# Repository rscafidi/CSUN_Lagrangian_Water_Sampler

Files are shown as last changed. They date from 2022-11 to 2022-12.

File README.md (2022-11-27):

# CSUN Lagrangian Water Sampler
Microcontroller code for the CSUN Lagrangian Water Sampler Project

This project was to fix a maker device created for California State University, Northridge.  The device runs using a Arduino compatible Mini Ultra 8Mhz microcontroller with ATmega328P processor.  The device controlls two peristaltic water pumps for two periods of time during each day.  Based on comments in the original code, it was originally created by Vincent Moriarty on June 29, 2016.  Since that time, the real time clock (DS3231) used to keep time in-between board power failures had run out of power causing the clock to reset.  As such, the pumps stopped working on their intended schedule.  During troubleshooting, the device was rendered inoperable and users were unable to reset the time.

The device was also created without any technical documentation.  This project scope was to understand the original circuit, troubleshoot the software and hardware, and restore it to original functionality.  Additional tasks are to document the circuit, components, and code and create a manual for how to reflash the code and restore it to operating state.

The code was completely rewritten but the original functionality was mostly retained.  The major change is that the new code will check for the Oscillator Stop Flag bit every time the controller boots.  This bit keeps track of when the real time clock oscillator stops, meaning the time is most likely not accurate.  If the OSF bit is detected as logical 1, the board goes into a LED flash loop to alert the user there is a problem.

Several other changes have been made to make the code easier to understand and modify.  The original code is retained in this repository for historical records.

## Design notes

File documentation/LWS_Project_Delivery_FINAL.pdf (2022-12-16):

1 | P a g e

# LAGRANGIAN WATER SAMPLER

PROJECT DELIVERY – FINAL DELIVERY

PREPARED FOR:

## CALIFORNIA STATE UNIVERSITY, NORTHRIDGE

Prepared by:

Richard E Scafidi – Software Engineer

richard@scafidi.dev

2 | P a g e

TABLE OF CONTENTS

3 | P a g e

ORIGINAL PROPOSAL

EXECUTIVE SUMMARY

The Lagrangian Water Sampler (LWS) is a custom-made device, created under the direction of California State University, Northridge (CSUN), who is hereon known as the Customer in this proposal. The LWS is used for automated collection of water samples at specific time intervals throughout each day, indefinitely while the onboard battery is still powering the device. The device was designed to be fully submerged under water at depths of approximately two to three meters. The device uses an Arduino based microcontroller and electronic components to control two water pumps on specifically programmed intervals. The device is powered by several large removable batteries. Recently, the device has become inoperable and troubleshooting attempts that were made to restore the device were not successful. CSUN is requesting to have the device restored to original functionality, and to provide technical documentation for the electronic circuitry, component design, and microcontroller code maintenance procedures to facilitate future maintenance efforts.

PROJECT SCOPE

The scope of this project is as follows:

- Examine, troubleshoot, and understand the original electronic circuitry.
- Design, assemble and test fixes to restore the system to functionality described in the Functional Requirements section.
- Document electronic circuit design and functionality.
- Document microcontroller source code and code flashing/building procedures.
- Document all electronic components within the system including part type, number and function/use case where possible.
- Testing is limited to electronic components and microcontroller programming only. The original waterproof housing will not be provided for testing and as such will not be a part of the test cases.
- There will be no continued support for the device after delivery of the functional device and documentation under this proposal.

4 | P a g e

PROJECT DELIVERABLES TIMELINE
The estimated timeline for deliverables is as follows:
Deliverable Name | Description | No Later Than Date
Feasibility Report | This is a single document that outlines the technical work that will need to be done after examining the device, and will deliver a statement on whether or not the planned project objectives can be delivered by the desired final deliverable date. | 31 August 2022
Project Update Briefs | If the project continues beyond the Feasibility date, project update briefs will be held on a recurring basis. These will be written reports that outline the current state of the project including progress, delays, and any other information. It will also include demonstrations of any functionality in order to ensure the device is being designed to meet the customer’s expectations. | Bi-weekly for the duration of the project
Post-testing Report and Demonstration | When the engineering team determines the project has met all documented requirements, a final testing report will be delivered. This report will be accompanied by a product demonstration to validate customer requirements have been met. | 15 November 2022
Documentation Validation | If the device is validated by the customer, the next deliverable will be product documentation to include parts lists, electronic diagram documentation, troubleshooting documentation, and code documentation. | 1 December 2022
Delivery of hardware and documentation artifacts | After the documentation is validated, the device will be returned to the customer along with all documentation artifacts. At this time the project will be considered closed. | 15 December 2022

Changes to the project may affect the above timeline. Adding new requirements may push the project beyond the desired completion timeline of December 2022. A best effort will be made to inform the customer of any such potential impacts.

5 | P a g e

BUDGET
This project is estimated to require between thirty (30) to forty (40) hours of engineering time for troubleshooting, repair, documentation and testing of the product. It will also potentially require acquisition of new electronic components. The budget estimates are outlined below. For all material costs, an estimate is given now. At the time of delivery and payment, actual receipts for any material item will be provided and the cost will be adjusted to match. The material estimates below are conservative estimates.
Item | Cost per Unit | Quantity / Type | Total
Engineering Time | $45 | 35 Hours | $1575
Electronic components | $150 | - | $150
Grant Total Estimated | | | $1725

If, after the project feasibility report, it is determined that the time estimated will vary plus or minus 10%, the Customer will be notified for approval to continue.

6 | P a g e

FUNCTIONAL REQUIREMENTS
Functional requirements are specific requirements that the system must meet to be considered complete. Below is a list of functional requirements.
- The system must be functional in an underwater environment at depths of two to three meters. This requirement will not be tested due to original housing unavailable for testing. No modifications are planned that would interfere with the original housing waterproofing capabilities.
- The system must run on the provided battery supply which outputs 12.5 volts.
- The system must use local time to operate on the following schedule:
o Activation of Pump 1 from local time 10:00 AM until 4:00 PM
o Activation of Pump 2 from local time 10:00 PM until 4:00 AM

NON-FUNCTIONAL REQUIREMENTS
Non-functional requirements are requirements not specifically related to a function of the device itself. Below is a list of non-functional requirements.
- The documentation provided will be in English.
- The documentation provided will include technical and non-technical aspects of the system, including each component, the function and use case within the system, and technical documentation for any source code provided.

7 | P a g e

DELIVERY REVIEW

DELIVERABLE SCHEDULE RESULTS

Deliverable Name | No Later Than Date | Outcome
Feasibility Report | 31 August 2022 | No report was generated. Verbal discussion with the customer resulted in simply fixing the functionality rather than redesigning the entire product. Due to the dramatic reduction in scope, a full report on how feasible a new product would be and what it would look like was not necessary.
Project Update Briefs | Bi-weekly for the duration of the project | We did not adhere to the bi-weekly updates on a regular basis, but we did provide casual updates on progress.
Post-testing Report and Demonstration | 15 November 2022 | This timeline was not achieved with the Customer, but extensive testing was done in-house by this date.
Documentation Validation | 1 December 2022 | All documentation was submitted to Customer on 28 November for validation.
Delivery of hardware and documentation artifacts | 15 December 2022 | One control unit will be delivered by 1 December and the second unit will be delivered by 20 December, pending any feedback from the Customer. Customer notified of final delivery and the new date is acceptable.

TOTAL COST TO DATE

Item | Actual Cost | Actual Quantity | Actual Total
Engineering Time | $45 | 32 | $1,440
Electronic components | $190.37 | - | $190.37
Shipping | $24.27 | - | $24.27
Grand Total | | | $1,654.64

*Note that extra materials were ordered and will be delivered to Customer for future repairs if necessary. Some components ordered will be retained for testing.

8 | P a g e

USER ACCEPTANCE TESTING

One Lagrangian Water Sampler unit was returned to the Customer by 1 December to validate project deliverables. The project deliverables consist of all documentation, along with one unit to test in the field.

Field testing was conducted, and no issues were reported. User acceptance testing considered to be completed. Second unit shipped on 16 December and will arrive no later than 20 December.

9 | P a g e

PRODUCT DOCUMENTATION

Below is a summary of the documentation provided as part of this project.

Appendix A – Circuit Diagram

Appendix B – Testing Report

Appendix C – Troubleshooting Manual

Appendix G – Bill of Materials

Appendix H – Material Cost Receipts

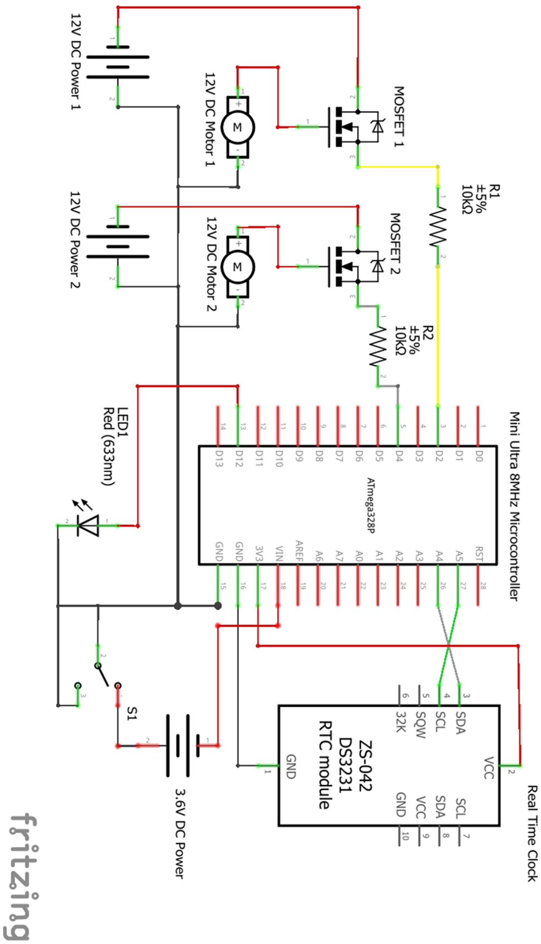
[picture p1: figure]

10 | P a g e

APPENDIX A – CIRCUIT DIAGRAM

11 | P a g e

APPENDIX B – TESTING REPORT

CONTROL UNIT 1 TEST RESULTS
Component | Results
LED | Pass
MOSFET Transistor 1 | Pass
MOSFET Transistor 2 | Pass
DS3231 Real Time clock | Pass
3v Clock battery | Fail
Microcontroller pin 3 | Fail
Microcontroller pin 5 | Pass
Microcontroller VIN | Pass
Microcontroller FTDI Header | Pass
Microcontroller Ground | Pass
Microcontroller pin A4 | Pass
Microcontroller pin A5 | Pass
Microcontroller 3.3v Power Supply | Pass

CONTROL UNIT 2 TEST RESULTS
Component | Results
LED | Pass
MOSFET Transistor 1 | Pass
MOSFET Transistor 2 | Pass
DS3231 Real Time clock | Pass
3v Clock battery | Fail
Microcontroller pin 3 | Pass
Microcontroller pin 5 | Pass
Microcontroller VIN | Pass
Microcontroller FTDI Header | Pass
Microcontroller Ground | Pass
Microcontroller pin A4 | Pass
Microcontroller pin A5 | Pass
Microcontroller 3.3v Power Supply | Pass

The components were tested on both pump control devices provided. For one control device, the only defective part was the 2032 3v watch battery powering the DS3231 real time clock. For the other, there is a voltage leak within the A328P processor causing pin 3 to be in HIGH state while the board is powered. This in turn keeps the MOSFET open, which will keep pump 1 on. A replacement microcontroller was ordered and soldered in place to restore functionality to the second controller. The 2032 3v watch battery was also bad on the second controller. Both watch batteries were replaced.

12 | P a g e

The code was completely rewritten for several reasons. First, the real time clock can track when a power failure has occurred, a feature which was previously not utilized. This feature was incorporated into the refactoring of the code to put the controller into a state such that normal operation will not proceed until the problem is addressed. The LED on pin 12 will flash continuously, which should alert the user that something is wrong with the controller. The maintenance manual walks through how to troubleshoot and restore the device to working order.

The second reason for refactoring is to make the code more readable. Detailed comments have been provided within the code to explain key portions of functionality. Additionally, the time control structure was rewritten to make it simpler to understand and modify. Outside of the comments, the code itself has been written in a manner to increase self-documentation, which will make it easier for users to read and change if necessary.

The final change relates to the inclusion of preprocessor directives to change the program execution behavior by simply commenting or uncommenting single variables. This again makes it easier to put the microcontroller into various testing states as well as enhancing the method of syncing the clock. The following page contains steps used to test each component with the new code.

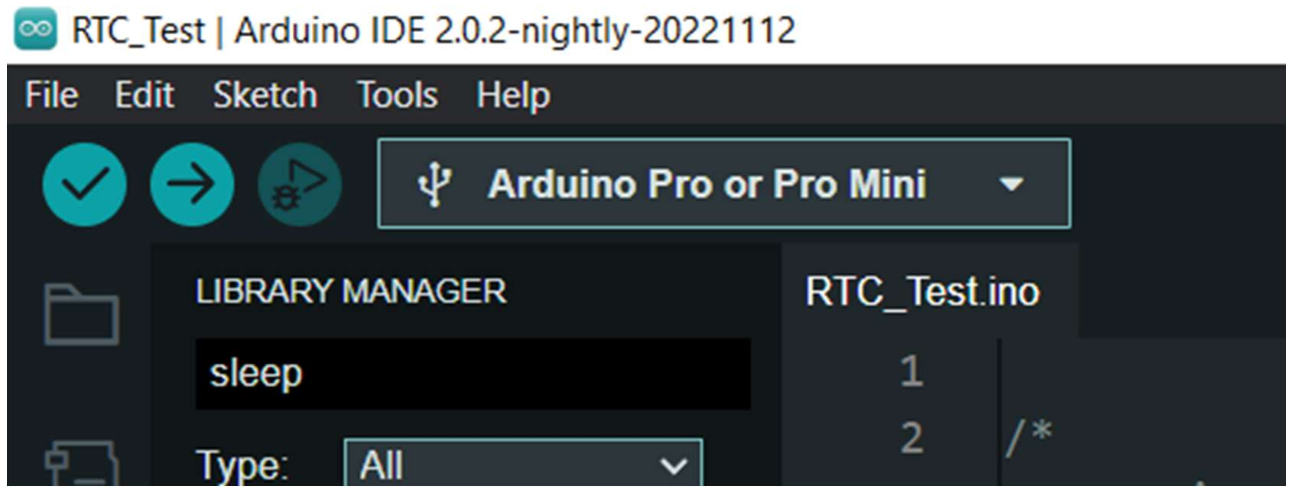
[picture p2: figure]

13 | P a g e

APPENDIX C – TROUBLESHOOTING MANUAL

TESTING DEPENDENCIES
Dependencies used in testing:
Adafruit RTClib library v2.1.1
Adafruit SleepyDog library v1.6.3
Standard Wire library

FLASHING CODE TO THE MICROCONTROLLER
The code is available on github at the following repository: https://github.com/rscafidi/CSUN_Lagrangian_Water_Sampler
Setting up Arduino IDE and loading the Pump Timer sketch
1. Open the Pump_Timer_MOSFET_Sleeper.ino sketch within the Arduino IDE.
a. Launch Arduino IDE, then go to File > Open > navigate to the .ino file
2. Set the IDE to the controller model and processor.
a. Connect the microcontroller to your PC with the USB header pin connector.
b. Click the COM port selector dropdown

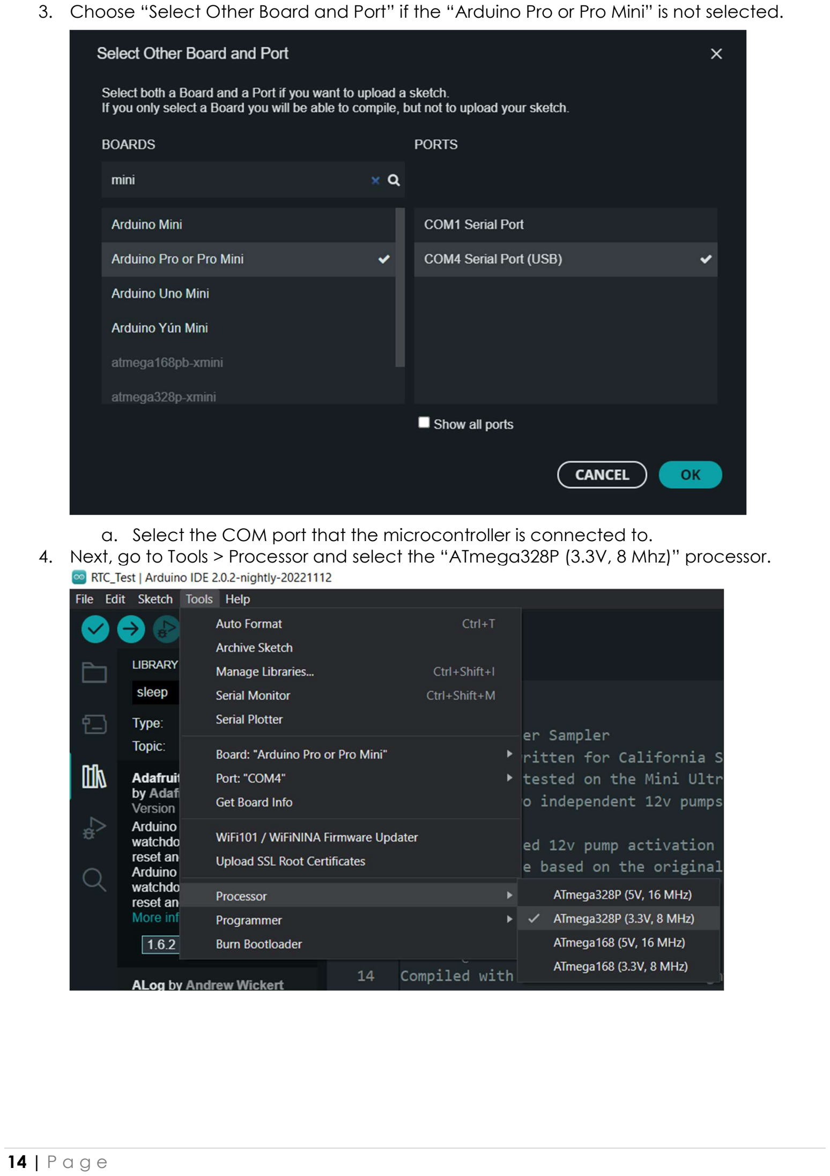
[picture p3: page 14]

14 | P a g e
3. Choose “Select Other Board and Port” if the “Arduino Pro or Pro Mini” is not selected.
a. Select the COM port that the microcontroller is connected to.
4. Next, go to Tools > Processor and select the “ATmega328P (3.3V, 8 Mhz)” processor.

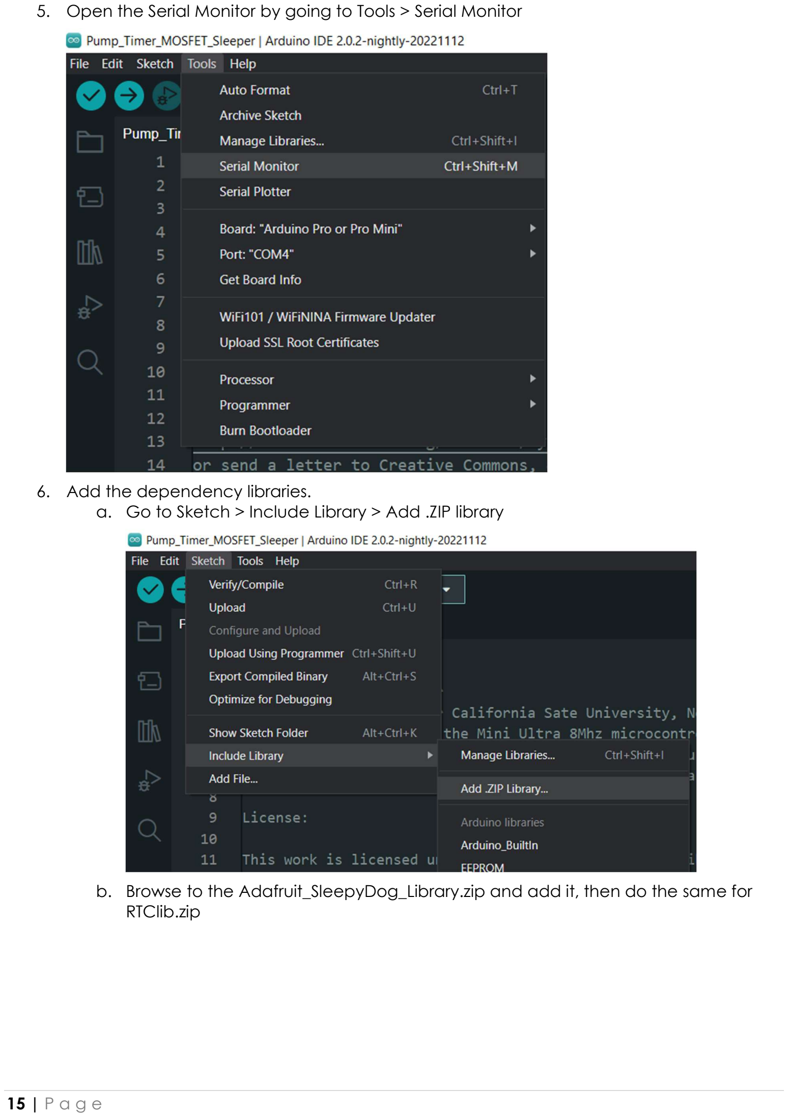
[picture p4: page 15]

15 | P a g e

### 5. Open the Serial Monitor by going to Tools > Serial Monitor

6. Add the dependency libraries.
a. Go to Sketch > Include Library > Add .ZIP library
b. Browse to the Adafruit_SleepyDog_Library.zip and add it, then do the same for RTClib.zip

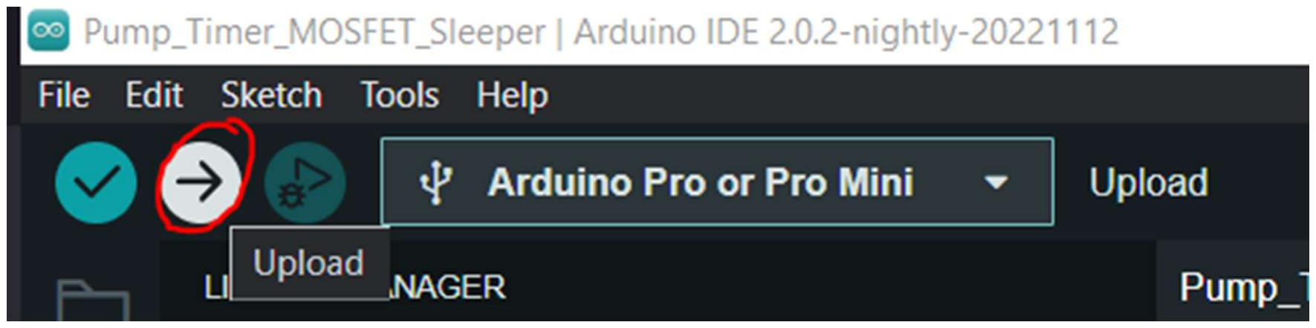
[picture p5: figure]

16 | P a g e
c. Note you can also install libraries via the library manager within the Arduino IDE but they were included in case dependencies change in the future.

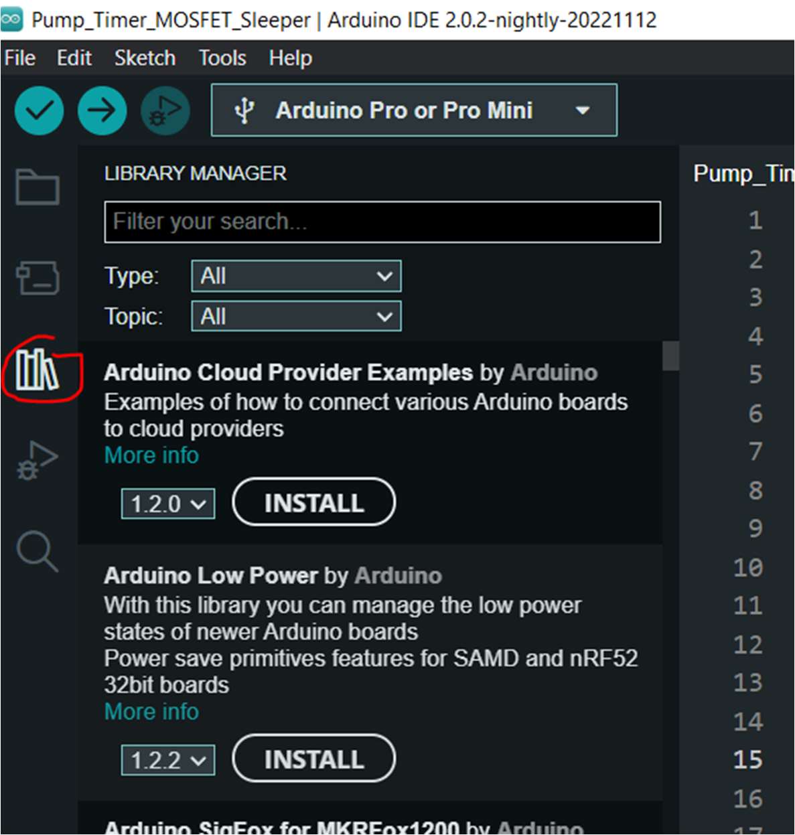
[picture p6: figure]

7. Put the controller into CODE_DEBUG_MODE by uncommenting line 36.
8. Click the Upload button to compile and load the program onto the microcontroller.
9. The Output tab will give you status on the compilation and upload. Note that if you see “Access is denied” on your COM port, try uploading again. Sometimes the COM port is busy and won’t let the PC talk over it temporarily. It could also be giving you that error if you have the wrong COM port selected.

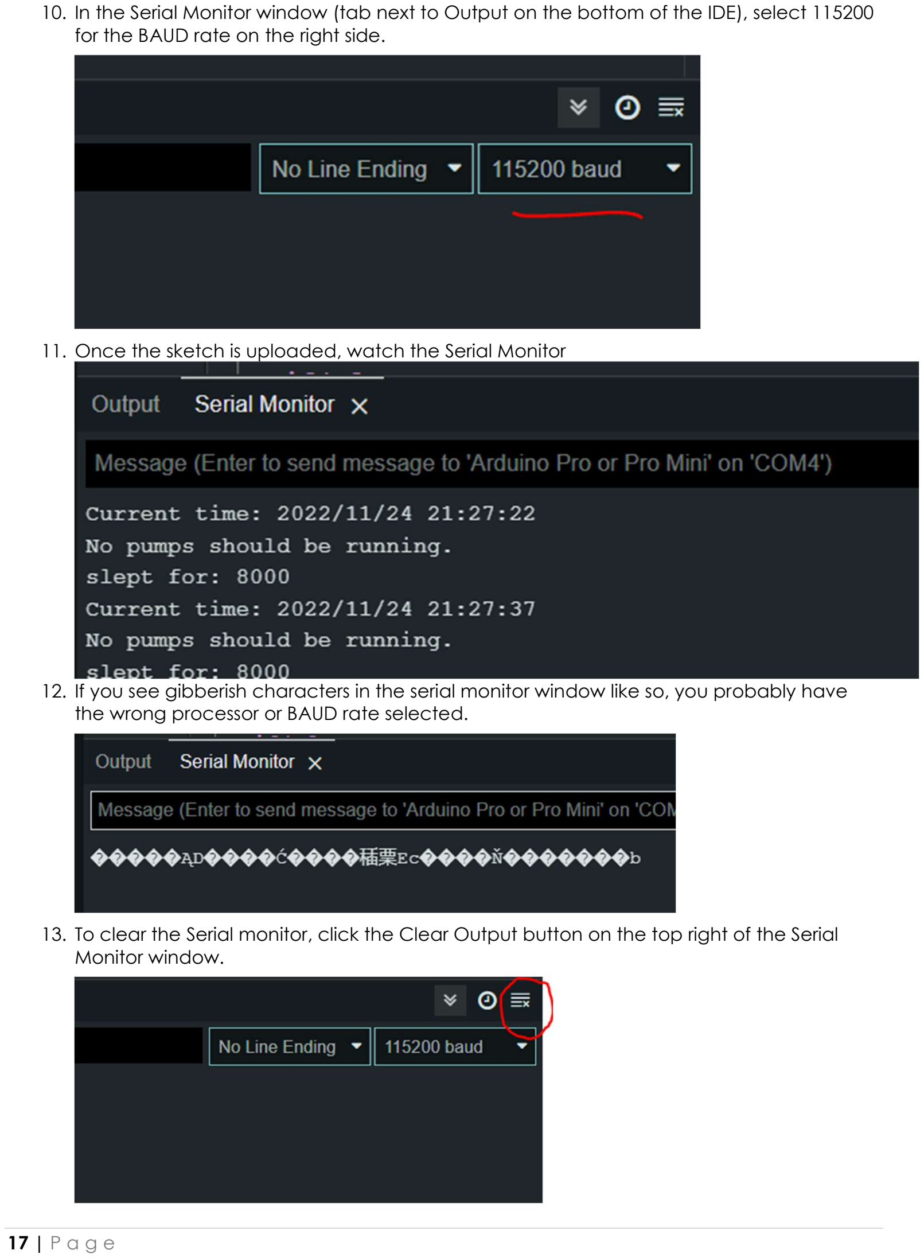
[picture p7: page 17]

17 | P a g e
10. In the Serial Monitor window (tab next to Output on the bottom of the IDE), select 115200 for the BAUD rate on the right side.

### 11. Once the sketch is uploaded, watch the Serial Monitor

12. If you see gibberish characters in the serial monitor window like so, you probably have the wrong processor or BAUD rate selected.
13. To clear the Serial monitor, click the Clear Output button on the top right of the Serial Monitor window.

18 | P a g e

LED LIGHT STATUS CODES

The LED light connected to pin 12 will flash in different patterns indicating various conditions of the controller.

LED Pattern | Meaning
Rapid blinking, not stopping | The microcontroller has encountered an error state, or the clock oscillator has been interrupted.
5 sets of 3 bursts | The microcontroller is in circuit debugging mode or clock sync mode. Program execution will not continue in these modes. Code must be recompiled and flashed with the control variables commented out.
20 bursts | The pumps are reporting as on during the scheduled hours they should be inactive. Troubleshooting required.
Single blink every ~10 minutes (seemingly no blink) | The microcontroller is operating normally and the pumps are both off.
Single blink every ~5 seconds | The microcontroller is operating normally and one of the pumps is active.

SWITCHING CONTROLLER MODES

The controller has three non-standard modes programmed that are controlled by commenting and uncommenting the associated control variables, starting on line 30. The first mode (CODE_DEBUG_MODE) will compile the code to produce Serial output strings that can be helpful for debugging so you can view the Serial Monitor for information. The second mode (CIRCUIT_DEBUG_MODE) will compile the code such that pump 1 and 2 will alternate being on for 5 seconds each. This can be useful for troubleshooting during times that the pumps won’t normally run. The third mode (CLOCK_SYNC_MODE) is used when the DS3231 real time clock has encountered a power interruption and needs to be resynced. This mode will reset the flags indicating power interruption occurred and will sync the time with the date and time that the application was last programmed. Note that for CIRCUIT_DEBUG and CLOCK_SYNC modes, it is critical to recompile the code with these modes commented out or the normal state will never resume. CODE_DEBUG_MODE can be used during normal operation, but it should be commented out as well when you are not actively debugging things.

19 | P a g e

CHANGING THE SCHEDULE BEHAVIOR

The original requirements specified that pump 1 should run from 10AM until 4PM, and pump 2 should run from 10PM until 4AM. The current program will accomplish this schedule. It is possible to change the schedule, but it may require some slight re-programming of the time control logic.

Constants used for the start and stop times for each pump are defined on lines 74 to 78. Shifting the hours is relatively easy. However, if you must add minutes to the schedule, you will have to evaluate the pump control logic and add in the checks for minutes. The current minute is accessible using now.minute() similar to how the hour was retrieved. The control logic is defined on lines 455 to 480.

With the current control logic, the pumps will activate within 10 minutes of the appropriate hour changing. It is possible to reach a higher degree of accuracy if required but it will take more power.

CHANGING BOARD SLEEP TIME
The pump activation will be plus or minus the setting for sleep minutes (constant variable SLEEP_SECONDS defined on line 79). This equates to 10 minutes, which appears to be the previous behavior based on previous code. This means that, in the worst case, the pump could activate up to 10 minutes past the start time. If higher accuracy is desired, simply reduce the SLEEP_SECONDS variable and recompile the code. Note that lower sleep time will increase power consumption.

TROUBLESHOOTING
1. Edit code to uncomment line 45, to enable CIRCUIT_DEBUG_MODE.
2. Compile and upload the code to the microcontroller.
3. Ensure a 12v power source is connected to the MOSFET transistors.
4. Verify the 5 bursts of 3 flashes on the LED, indicating the controller is in a special control mode.
a. Each pump will cycle ON for 5 seconds before repeating the flash cycle. Check that each pump operates.
b. If the LED never illuminates, check the board power on the VIN pin, a minimum of 3.3v is required.
c. If the board is powered and the code successfully uploaded but there are no LED flashes, check the signal on pin 12. If pin 12 never goes HIGH, there may be a problem with the microcontroller.

### 5. If the pumps are not connected, use a multi-meter to check the voltage on the output

side of the MOSFET transistor. Place one lead on GROUND and place the other on the positive side of the MOSFET transistor output. Wait for the controller to cycle, a minimum of 7 seconds if it is not active when you first check.

20 | P a g e
a. If the output never reads 12v, trace the signal from pin 3 (or 5). If the voltage is cycling on the pin wire but the output never cycles to 12v, there is a problem with the MOSFET transistor, and it should be replaced.
6. Repeat for the second MOSFET transistor.
7. Check the DS3231 onboard LED. It should be illuminated when the board is powered.
a. If desired, put the board into CODE_DEBUG_MODE, compile and upload, and watch the serial output to ensure the time is correct.
b. If time needs to be corrected, uncomment the CLOCK_SYNC_MODE control variable, and flash the code again.
i. IMPORTANT: You must comment out the CLOCK_SYNC_MODE control variable and flash the code again before the microcontroller boots again. When CLOCK_SYNC_MODE is active, it will always use the last compiled time to set the real time clock. If you wait an hour and the board reboots, the clock will now be off by one hour.
8. Assuming you have been testing while the microcontroller is connected to the PC, restore the normal operational mode by commenting out all control variables and flashing the code again. Remove the controller from the USB/FTDI header and connect to 3.6v battery supply.
a. Verify the LED is flashing once every 15 seconds if the time is outside of pump operational hours, or once per 5 seconds if the time is within pump operational hours.
9. Ensure the switch works to turn the main board off.
10. Turn the main board back on. Ensure the LED pattern continues to read a normal state.

### 11. If the LED ever enters a quick pulse that does not stop, an error state has been

encountered.
a. Most likely, the real time clock has lost power.
b. Check the 3v battery supply, replace if necessary.
c. Flash code again with CLOCK_SYNC_MODE and CODE_DEBUG_MODE uncommented.
d. Watch the serial output and make sure it goes back to a normal state.
e. Comment the special control variables and flash code, check LED again and power cycle the board.
12. If the board is properly resetting the clock registers (success messages when board is in CLOCK_SYNC_MODE) but the real time clock is losing power in between board cycles with a known good 3v battery, this could indicate a problem with the real time clock. Recommend replacing the module.

21 | P a g e

APPENDIX D – BILL OF MATERIALS

Below are the items that comprise the Lagrangian Water Sampler. These parts were provided by CSUN and in some cases, replacements were ordered. This list includes each component with applicable part numbers where possible.

Item Friendly Name | Part Number or ID | Functional Description
Mini Ultra 8Mhz Microcontroller | ATMega328P 8Mhz 3.3v | Microcontroller for executing code to control LED and pumps
MOSFET Transistor x2 | FQP30N06L | Transistor to open circuit to 12V power in order to power the pumps
Real Time Clock module | DS3231 | Real time clock with battery power supply to retain time in between board power cycles
LED | Standard | Light emitting diode to be used for status indications
FTDI USB cable | FTDI USB to TTL Serial Female Socket Header | Connect microcontroller to computer with Arduino IDE, for flashing new code to the controller
Watch battery | 2032 3v battery | For powering the RTC module
Standard electronics wiring | 22 AWG electronic wiring | For connecting components
Board power supply | 3.6v Li battery | For powering the microcontroller
Welco water pump x2 | WP10 Peristaltic Pump | For pumping water
12v Power Supply | - | For powering pumps
Bread Board | - | For connecting and soldering all components
10k Ohm Resistors | - | Wired with transistor
Custom Plexiglass Case | - | Housing for control unit
D Cell size battery holder | - For holding the board power supply.

Sources:

https://smile.amazon.com/gp/product/B004UHUGGC/ref=ppx_od_dt_b_asin_title_s00?ie=UTF8&psc=1

https://smile.amazon.com/gp/product/B07PKKY8BX/ref=ppx_yo_dt_b_asin_title_o01_s00?ie=UTF8&psc=1

https://smile.amazon.com/gp/product/B073QMYKDM/ref=ppx_yo_dt_b_asin_title_o01_s01?ie=UTF8&psc=1

https://smile.amazon.com/gp/product/B08B8WRQP1/ref=ppx_yo_dt_b_asin_title_o02_s00?ie=UTF8&psc=1

https://smile.amazon.com/dp/B07Q7NZTQS?psc=1&ref=ppx_yo2ov_dt_b_product_details

https://www.rocketscream.com/blog/product/mini-ultra-8-mhz-arduino-compatible/

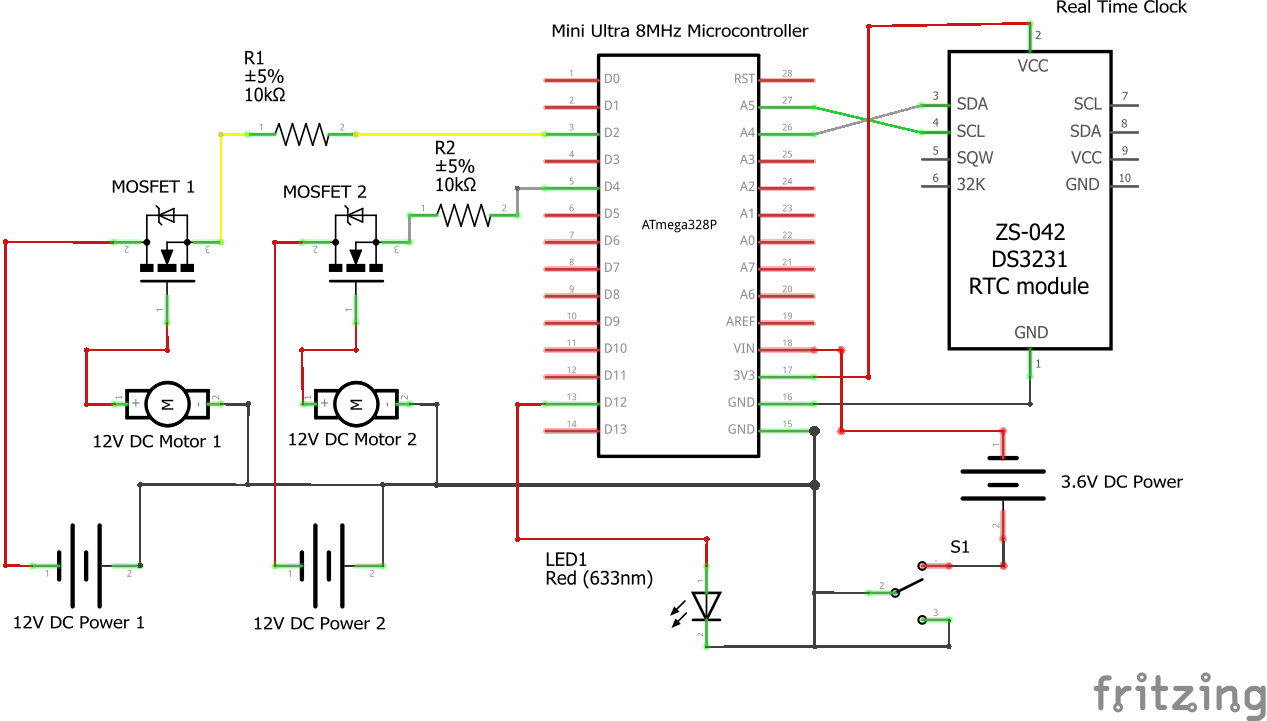
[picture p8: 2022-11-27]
documentation/LagrangianWaterSampler_CircuitDiagram.png

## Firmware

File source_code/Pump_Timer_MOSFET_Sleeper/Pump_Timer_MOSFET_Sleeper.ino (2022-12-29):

/*
Lagrangian Water Sampler
This code is written for California Sate University, Northridge.
This code was tested on the Mini Ultra 8Mhz microcontroller with ATmegaA328P processor.
It controls two independent 12v pumps on a schedule, using the DS3231 real time clock.
This code was shipped with electronic schematics and a troubleshooting / maintenance manual.

License:

This work is licensed under the Creative Commons Attribution-ShareAlike 3.0 United 
States License. To view a copy of this license, visit: 
http://creativecommons.org/licenses/by-sa/3.0/us/ 
or send a letter to Creative Commons, 444 Castro Street, Suite 900, Mountain View, 
California, 94041, USA.

Refactored code based on the original sketch by Vincent Moriarty, dated June 29 2016

Author:  Richard Scafidi
Date: 27 November 2022
richard@scafidi.dev
Compiled with Arduino IDE v2.0.2-nightly-20221112


*/
#include <RTClib.h>                 // Adafruit RTClib library      v2.1.1
#include <Adafruit_SleepyDog.h>     // Adafruit SleepyDog library   v1.6.3
#include <Wire.h>                   // Standard Wire library

/* =================== CONTROL CONSTANTS (uncomment these to change program behavior) =================
=======================================================================================================
Defining CODE_DEBUG_MODE will compile additional Serial prints and information
to aide in the troubleshooting process.  Uncomment this line and recompile 
*/ 
// *  *  *  *  *  *  *  *  *  *  *  *  *  *  *  *  *  *  *  *  *  *  *  *  *  *  *  *  
//#define CODE_DEBUG_MODE // UNCOMMENT THIS FOR SERIAL DEBUG MESSAGES
// *  *  *  *  *  *  *  *  *  *  *  *  *  *  *  *  *  *  *  *  *  *  *  *  *  *  *  *  

/*
Defining CIRCUIT_DEBUG_MODE will enter the board into a loop for troubleshooting board circuits.  This mode
will activate each pin/pump circuit and LED on a short recurring loop, allowing you to use a milti-meter to test the physical
circuit to ensure the MOSFETs are working correctly, as well as the pins on the board to activate them.
*/
// *  *  *  *  *  *  *  *  *  *  *  *  *  *  *  *  *  *  *  *  *  *  *  *  *  *  *  *  
//#define CIRCUIT_DEBUG_MODE // UNCOMMENT THIS FOR CIRCUIT TROUBLESHOOTING
// *  *  *  *  *  *  *  *  *  *  *  *  *  *  *  *  *  *  *  *  *  *  *  *  *  *  *  *  

/*
Defining CLOCK_SYNC_MODE will synchronize the clock with the last compiled time, and
attempt to reset the real time clock DS3231 registries to clear any invalid power state flags.
WARNING: After syncing clock with CLOCK_SYNC_MODE uncommented, recompile the code again after
commenting this line out.  This will ensure the registry is only reset once and not every time
the microcontroller reboots.
*/
// *  *  *  *  *  *  *  *  *  *  *  *  *  *  *  *  *  *  *  *  *  *  *  *  *  *  *  *  
//#define CLOCK_SYNC_MODE // UNCOMMENT THIS TO SYNC CLOCK AND CLEAR OSCILLATOR REGISTRY FLAGS ** MUST COMMENT BACK OUT AND RECOMPILE AFTER SUCCESSFUL SYNC!
// *  *  *  *  *  *  *  *  *  *  *  *  *  *  *  *  *  *  *  *  *  *  *  *  *  *  *  *  
// ==================== END CONTROL CONSTANTS =======================================================





// ==================== CONSTANTS ===================================================================
// Constants defined for the DS3231 registry and I2C slave addresses.  These come from the official
// data sheet for the DS3231.
#define REAL_TIME_CLOCK_SLAVE_ADDRESS 0x68
#define OSF_REGISTER_ADDRESS 0xF
#define EOSC_REGISTER_ADDRESS 0xE

// The FLAG_NORMAL_STATE is what the registry value should be when the oscillator is working normally.
// Per the data sheet, when OSF reads 1, the oscillator has been interrupted.  EOSC value of 1 means the
// oscillator will not run on battery power.
const int FLAG_NORMAL_STATE = 0;
const int START_HOUR_1 = 10; // 10am
const int STOP_HOUR_1 = 16; // 4pm
const int START_HOUR_2 = 22;  // 10pm
const int STOP_HOUR_2 = 4; // 4am
const int SLEEP_SECONDS = 600; // 10 minutes of sleep, adjust to the time you want the board to sleep for when pumps are off.
const int MAX_SLEEP_TIME_ALLOWED_BY_CONTROLLER = 8; // do not change this, it is a limitation of the microcontroller

// ================== Object Instantiations =========================================================

// Gives a handle for the RTC library, used for the adjust() function
// to grab time from local PC and to store time for checking when to activate pumps
RTC_DS1307 RTC;

// ==================== PIN MAPPINGS =================================================================
int LED = 12;
int pump1 = 3;
int pump2 = 5;



// =================== FUNCTION DEFINITIONS ========================================================== 
/*
Below are a set of functions for checking and setting the Oscillator Stop Flag (OSF) bit, the Enable OScillator (EOSC) bit,
and dealing with sleeping/waking and checking the time for the pumps and activating/deactivating the pumps.
The OSF bit is set to logical 1 when the real time clock oscillator has stopped.  This indicates a power failure or interruption
on the real time clock, and likely the battery needs to be checked.  The EOSC bit controls whether the oscillator will run when
the real time clock is powered by battery.  With EOSC set to 1, the clock will NOT progress when on battery only voltage, meaning
the clock will not keep time.  Both the OSF and EOSC bit must be set to logical 0 in order to persist time between main board power cycling.
*/

/*
The flashLEDCode is a helper function that flashes the LED to act as a visual indicator for exceptions.
LED pattern definitions:
- Rapid blinking, not stopping
    The microcontroller has encountered an error state, or the clock oscillator has been interrupted.
    Both cases need manual intervention to remedy.
- 5 sets of 3 bursts
    The microcontroller is in circuit debugging mode or clock sync mode.  Program execution will not continue in these modes.  Code must
    be recompiled and flashed with the control variables commented out.
- 20 bursts
    The pumps are reporting as on during the schedule hours they should be inactive.  Troubleshooting required.
- Single blink every ~10 minutes, seemingly no blink (depending on SLEEP_SECONDS constant)
    The microcontroller is operating normally and the pumps are both disabled.
- Single blink every ~5 seconds
    The microcontroller is operating normally and one of the pumps is active.
*/
void flashLEDCode(int indicatorCycles, int indicatorBursts) {
    
    for (int i = 0; i < indicatorCycles; ++i) {
        for (int j = 0; j < indicatorBursts; ++j) {
            digitalWrite(LED, HIGH);
            delay(100);
            digitalWrite(LED, LOW);
            delay(100);
        }
        delay(500);
    }
}

/*
The clearBit function takes an I2C address, registry address, specific bit, and buffer read size and sets
the bit to the FLAG_NORMAL_STATE bit.  It will check for the successful bit writing after attempting to change.
This is a helper function for the OSF and EOSC bit resetting.
Returns TRUE if the bit was successfully set to the FLAG_NORMAL_STATE value
*/ 
bool clearBit(int I2CslaveAddress, int registryAddress, int bitNumber, int readSize) {
    bool clearSuccess = true;

    #ifdef CODE_DEBUG_MODE
        Serial.println("Attempting to clear registry bits...");
    #endif

    Wire.beginTransmission(I2CslaveAddress);
    Wire.write(registryAddress);
    Wire.endTransmission(false);
    Wire.requestFrom(I2CslaveAddress,readSize);
    byte buf = Wire.read(); // storing the registry value in a buffer so we can manipulate the bits
    
    #ifdef CODE_DEBUG_MODE
        Serial.print("Registry bit value: ");
        Serial.println(bitRead(buf, bitNumber));
    #endif
    
    bitWrite(buf, bitNumber, FLAG_NORMAL_STATE); // Write the FLAG_NORMAL_STATE bit value to the buffer
    
    #ifdef CODE_DEBUG_MODE
        Serial.print("New value before write: ");
        Serial.println(bitRead(buf, bitNumber));
    #endif

    Wire.beginTransmission(I2CslaveAddress);
    Wire.write(registryAddress);
    Wire.write(buf);
    byte error = Wire.endTransmission();
    if (error) {
        #ifdef CODE_DEBUG_MODE
            Serial.println("Error on I2C Bus, registry bit status unknown.");
        #endif
        
        clearSuccess = false;
    }

    // Verify the bit was successfully written by checking the register one more time
    #ifdef CODE_DEBUG_MODE
        Serial.println("Verifying registry bit set...");
    #endif

    Wire.beginTransmission(I2CslaveAddress);
    Wire.write(registryAddress);
    Wire.endTransmission(false);
    Wire.requestFrom(I2CslaveAddress,readSize);
    buf = Wire.read();
    int bitFlag = bitRead(buf, bitNumber);
    if (bitFlag != FLAG_NORMAL_STATE) {
        #ifdef CODE_DEBUG_MODE
            Serial.println("bit value does not match FLAG_NORMAL_STATE, failed to set bit.");
        #endif
        clearSuccess = false;
    }
    Wire.endTransmission();

    return clearSuccess;
}

/*
The clearOscillatorBitFlags is a helper function for resetting the OSF and EOSC registry bits.
Returns TRUE on successful bit clearing.
*/
bool clearOscillatorBitFlags() {
    // call clear bit passing both the OSF and EOSC registers
    // returns true only IFF both bits successfully clear to logical value 0
    return (clearBit(REAL_TIME_CLOCK_SLAVE_ADDRESS, OSF_REGISTER_ADDRESS, 7, 1) && clearBit(REAL_TIME_CLOCK_SLAVE_ADDRESS, EOSC_REGISTER_ADDRESS, 7, 1));
}

/*
checkBit is a helper function for checking the state of the OSF and EOSC registry bits.
Returns TRUE if the flags match the defined FLAG_NORMAL_STATE.
*/
bool checkBit(int I2CslaveAddress, int registryAddress, int bitNumber, int readSize) {
    bool flagNormal = true;

    #ifdef CODE_DEBUG_MODE
        Serial.print("Reading bit - value is: ");
    #endif

    // This is the standard method to read a register on the I2C bus communication bus
    Wire.beginTransmission(I2CslaveAddress);
    Wire.write(registryAddress); // set the register to prepare to read
    Wire.endTransmission(false);  
    Wire.requestFrom(I2CslaveAddress, readSize); // read readSize byte(s) from the register
    byte registryBuffer = Wire.read();
    int bitFlag = bitRead(registryBuffer,bitNumber); // read the bitNumber'th bit of the register
    
    #ifdef CODE_DEBUG_MODE
        Serial.println(bitFlag);
    #endif
    
    if (bitFlag != FLAG_NORMAL_STATE) { // true if registry Buffer is 1, indicating oscillator was interrupted
        #ifdef CODE_DEBUG_MODE
        Serial.println(bitFlag);
        Serial.println("Bit flag indicates abnormal clock oscillator state.");
        #endif
        flagNormal = false;
    }

    return flagNormal;
}

/*
OSFBitIsNormal is a helper function for checking the OSF bit.
Returns TRUE if the OSF flag (bit 7 of the OSF registry) is 0 which indicates a normal state.
*/
bool OSFBitIsNormal() {
    return checkBit(REAL_TIME_CLOCK_SLAVE_ADDRESS, OSF_REGISTER_ADDRESS, 7, 1);
}

/*
EOSCBitIsNormal is a helper function for checking the OSF bit.
Returns TRUE if the OSF flag (bit 7 of the EOSC registry) is 0 which indicates a normal state.
*/
bool EOSCBitIsNormal() {
    return checkBit(REAL_TIME_CLOCK_SLAVE_ADDRESS, EOSC_REGISTER_ADDRESS, 7, 1);
}

/*
checkOscillatorNormalcy checks if either the OSF bit flag or EOSC bit flag have entered a non-normal state
which indicates a power interruption and clock time may be inaccurate.
Returns TRUE if the oscillator is functioning normally.
*/
bool checkOscillatorNormalcy() {
    bool oscillatorIsNormal = true;

    if (OSFBitIsNormal() && EOSCBitIsNormal()) { // Check both bits, if either returns false (abnormal state), alert
        oscillatorIsNormal = true;
    } else {
        oscillatorIsNormal = false;
    }
    return oscillatorIsNormal;
}
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

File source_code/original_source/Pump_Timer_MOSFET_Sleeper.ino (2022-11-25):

//Arthor- Vincent Moriarty
//Date- June 29 2016


/*License:

  This work is licensed under the Creative Commons Attribution-ShareAlike 3.0 United 
  States License. To view a copy of this license, visit: 
    http://creativecommons.org/licenses/by-sa/3.0/us/ 
  or send a letter to Creative Commons, 444 Castro Street, Suite 900, Mountain View, 
  California, 94041, USA.

  */
//The bellow code controlls two different peristaltic pumps (using MOSFETs)
//A RTC clock is used to keep time, with Start HR:MM and Stop HH:MM for each Pump
// Timer can handle overnight (passes 24 HR mark) controlling
//Power can be interupted to unit and pumps (as long as battery is good on RTC)


// Date and time functions using a DS3231 RTC connected via I2C and Wire Lib

#include <Wire.h>
#include <RTClib.h>  // Uses DateTime values
#include <TimeLib.h>
#include <stdio.h>
//#include <DS1307RTC.h>  // Uses time_t values
#include <DS3231.h> // Uses time_t values

//For sleep modes
#include <avr/sleep.h>
#include <avr/wdt.h>


// watchdog interrupt
ISR(WDT_vect) {
  wdt_disable();  // disable watchdog
}

void myWatchdogEnable(const byte interval) {
  MCUSR = 0;                       // reset various flags
  WDTCSR |= 0b00011000;            // see docs, set WDCE, WDE
  WDTCSR = 0b01000000 | interval;  // set WDIE, and appropriate delay

  wdt_reset();
  set_sleep_mode(SLEEP_MODE_PWR_DOWN);
  sleep_mode();  // now goes to Sleep and waits for the interrupt
}




//This is from the RTClib, not the DS1307RTC.h
DS3231 RTC;  // Only use if using a DS1307 (do not 'include DS1307' if using this- causes conflict)



// Start Time and End Times for PUMP 1 (NO LEADIN ZEROS--"8" not "08")
byte startHour1 = 10;  //10
byte startMinute1 = 0;
byte endHour1 = 16;  //16
byte endMinute1 = 0;


// Start and End Time for PUMP 2
byte startHour2 = 22;  //22
byte startMinute2 = 0;
byte endHour2 = 4;  //4
byte endMinute2 = 0;



//Define MOSFET Pin Locations (must be PWM pins)
int pump1 = 3;  //Define Pin for PUMP 1 (Day Time
int pump2 = 5;  //  Define Pin for PUMP 2 (Night Time)

//Define LED pin location
int LED = 12;



//Set Boolean values if Pump is running
boolean pump1Running = true;
boolean pump2Running = true;


//Define type "tmElements_t" and type "time_t"
//time_t variables store a the timestamps since 01/01/1970 (Unix epoch) which are easier to work with
//tmElements structures are more human friendly

//'tm' variable stores current time (used for both Pump 1 and Pump 2 controlls)
tmElements_t tm;
time_t now_;


//For Pump 1
tmElements_t tm_hour_start1;
tmElements_t tm_hour_end1;

time_t t_hour_start1;
time_t t_hour_end1;


//For Pump 2
tmElements_t tm_hour_start2;
tmElements_t tm_hour_end2;

time_t t_hour_start2;
time_t t_hour_end2;


//boolean for TRUE (1) or False (0) Whether or not to update time stamp
boolean update_tm1 = 1;

boolean update_tm2 = 1;
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

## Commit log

2022-11-21 First commit, code rework and data sheet files
    [CircuitDiagram.fzz]
2022-11-24 additional functions for clock checking, control for debug modes, beginning check for times to activate pump
2022-11-25 move .ino to folder with sketch name, required by arduino IDE
2022-11-27 add circuit diagram png and remove fritzig file
    [CircuitDiagram.fzz]
2022-11-28 Sleep modifications and add Serial prints
2022-12-10 add one more serial print for confirmation when registers are successfully reset.
2022-12-29 adjust comment for LED flashing function to be more accurate.
